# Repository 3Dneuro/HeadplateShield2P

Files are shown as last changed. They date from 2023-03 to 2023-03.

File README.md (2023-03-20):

# Headplate and light-blocking sleeve for 2P imaging
This system was designed to provide simple and reliable light shielding for 2-photon imaging in awake head-fixed mice (running on a 3D-treadmill with visual stimulation in our case). With this in mind, we optimized for the following criteria:

* No hand-made or improvised components that can add variability to the data quality of each experiment – so no putty, wax or tape.
* Simple connection between the animal’s headplate and the light shielding around the microscope lens, to prevent having to work close to the animal’s head, which can stress animals and impact task performance.
* Quick fastening mechanism (< 1 minute). Animals only have a limited time span for motivated, focused performance. We want to lose as little as possible of that time on setting up the imaging. Ideally, the time between putting the animal on the treadmill and beginning the first imaging sequence should be well below 10 minutes.
* Easy to ensure watertight seal with the skull to prevent leakage of fluid during imaging.
* Cheap and easy to replace/tweak if necessary.

We came up with a two-part solution. One is a circular headplate with a ring that rises up conically to fit around the microscope lens while providing a fluid reservoir for imaging with water-immersed objectives. The headplate has two connectors/holders on the side that can be used for stable head fixation (similar concept to Poort et al. 2015 Neuron, Havenith et al. 2019 Scientific Reports). It is easy to implant on the skull, and then remains stable and watertight for months.

The second component is a light-absorbing conical sleeve which was designed to fit with an Olympus 20x objective, and can be lowered below the rim of the implanted headplate once the animal is head-fixed under the microscope. Since the sleeve is designed to fit snugly underneath the rim of the headplate’s cone, it doesn’t require any extra fastening mechanisms apart from lowering it past the headplate’s rim, making it extremely quick and easy to use. In our experience, lowering the sleeve all the way to the base of the headplate eliminates all stray light in recordings.

A first version of this design was published as [10.5281/zenodo.4547658](https://zenodo.org/record/4547658#.ZBLb5XbMKUn). The current version is a parametric re-make of v1 that allows you to change relevant dimensions of the designs and adjust them to your needs (e.g. diameter and height of the sleeve).

# Parameters

> The parametric design was created in Autodesk Fusion 360. To edit the parameters described below, you will need to import the f3d file into Fusion 360. At time of publication, a free Fusion 360 license for academics/educators was available from Autodesk.

The design can be altered to your needs by modifying the parameters controlling the relevant dimensions (see the video below). The table below contains the parameter names, a description of their function and some relevant notes regarding their impact on the design. A graphical representation of the parameters is available in the form of two drawings, one of the [headplate](https://github.com/3Dneuro/HeadplateShield2P/blob/main/design%20files/Headplate%20drawing.pdf) and one of the [sleeve](https://github.com/3Dneuro/HeadplateShield2P/blob/main/design%20files/Sleeve%20drawing.pdf), that can be found in the design files folder (see preview image below). They demonstrate the precise, physical dimensions corresponding to the parameters. These drawings can be used to easily visualize and determine what parameters should be modified for the changes that you wish to make.

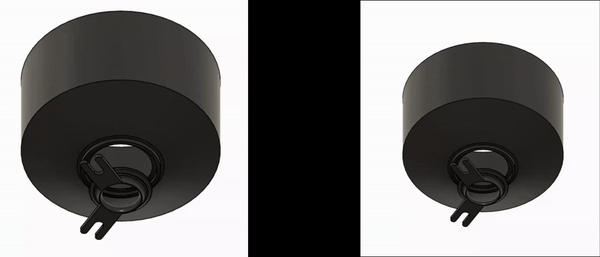
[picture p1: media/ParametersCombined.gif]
Effects of changing parameters #1
 

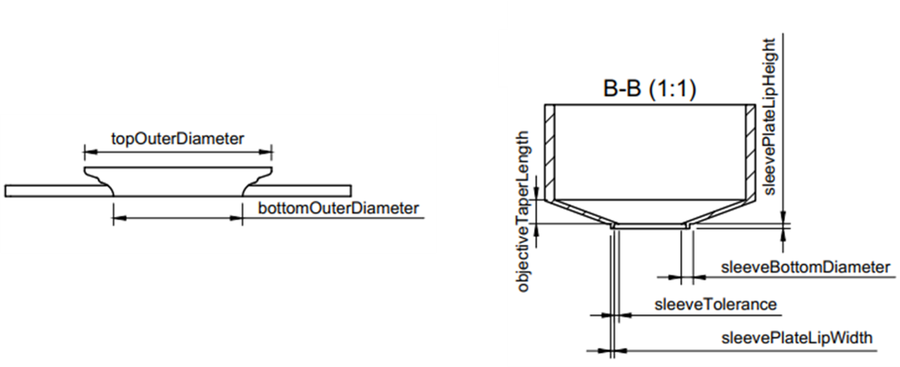
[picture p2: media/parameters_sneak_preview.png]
A selection of editable parameters


## Headplate
| Parameter               | Description                                                                                                       | Notes                                                                                                                                                                                                            |
| ----------------------- | ----------------------------------------------------------------------------------------------------------------- | ---------------------------------------------------------------------------------------------------------------------------------------------------------------------------------------------------------------- |
| bottomInnerDiameter     | The diameter in mm of the opening at the bottom of the headplate                                                  |                                                                                                                                                                                                                  |
| bottomOuterDiameter     | The outer diameter in mm of the bottom of the headplate                                                           |                                                                                                                                                                                                                  |
| topInnerDiameter        | The diameter in mm of the opening at top of the headplate                                                         |                                                                                                                                                                                                                  |
| topOuterDiameter        | The outer diameter in mm of the top of the headplate                                                              | Determines the diameter of the bottom opening in the sleeve as well, ensuring a natural light seal                                                                                                               |
| middleInnerDiameter     | The inner diameter in mm of the hole at the middle of the headplate                                               |                                                                                                                                                                                                                  |
| totalHeight             | The height in mm from the bottom of the headplate to the very top                                                 | Height includes the set height of the lip (topLipHeight)                                                                                                                                                         |
| topLipHeight            | The height in mm of the lip that sits at the top of the headplate                                                 |                                                                                                                                                                                                                  |
| holderLengthFromCenter  | The length in mm of the two holder arms taken with respect to the center of the headplate                         | Solely controls the length of the arms, start of screw openings/slots is not affected                                                                                                                            |
| holderWidth             | The width in mm of the holder arms                                                                                | Does not alter the diameter of the screw openings, can be used to widen or slim the two prongs of each holder                                                                                                    |
| holderOpeninngDiameter  | The diameter in mm of the screw openings in the holder arms                                                       | This determines what size screws should be used to fasten the headplate                                                                                                                                          |
| holderOpeningFromCenter | The distance in mm from the beginning of the screw opening to the center of the headplate                         | Can be used to move the start of the screw openings/slots to or from the center of the headplate                                                                                                                 |
| holderHeight            | The height in mm of the holder arms                                                                               | Height of the holders is limited with respect to the height of the headplate (totalHeight)                                                                                                                       |
| holderAngle             | The angle in degrees of the holder arms with respect to the z midline                                             | Holder configuration can be changed using this parameter. At certain angles, holders can be made to overlap if so desired                                                                                        |

## Sleeve
| Parameter               | Description                                                                                                       | Notes                                                                                                                                                                                                            |
| ----------------------- | ----------------------------------------------------------------------------------------------------------------- | ---------------------------------------------------------------------------------------------------------------------------------------------------------------------------------------------------------------- |
| wallThickness           | The thickness in mm of the walls of the sleeve                                                                    |                                                                                                                                                                                                                  |
| objectiveDiameter       | The inner diameter in mm of the sleeve                                                                            | Using this and objectiveTaperLength, the sleeve can be made to fit specific objectives                                                                                                                           |
| sleeveHeight            | The height in mm of the straight portion of the sleeve (excluding the taper thus)                                 | Can be used to have the sleeve run further up the objective                                                                                                                                                      |
| toleranceSleeve         | The space in mm between the lip on the sleeve and the lip on the headplate                                        | This parameter controls the distance between the sleeve and headplate and thus how well light is sealed out. Less tolerance means less light can reach the opening, however, resutling in less room for movement |
| objectiveTaperLength    | The vertical height in mm of the taper, to be measured from the start of the taper to the bottom of the objective | To ensure a correct fit, measure the distance from the start of the taper on the objective to the bottom as if it were on the midline                                                                            |
| sleeveBottomDiameter    | The outer diameter in mm of the bottom of the sleeve                                                              | Controls the flat area at the bottom of the sleeve, a higher outer diameter increases the surface area upon which the sealing lip is located allowing for more tolerance if needed                               |
| sleevePlateLipWidth     | The width in mm of the sealing lip at the bottom of the sleeve                                                    | The max width dependents on the surface area at the bottom of the sleeve, adjust sleeveBottomDiameter when required to do so                                                                                     |
| sleevePlateLipHeight    | The height in mm of the sealing lip at the bottom of the sleeve                                                   |                                                                                                                                                                                                                  |

# Manufacturing
While the headplate can be produced in a range of materials, we recommend machined aluminum, which is strong enough to ensure stable imaging-compatible head fixation while still being light. For test purposes, printing the headplate in a sturdy plastic can work well.
The sleeve can be made in any opaque plastic, preferably one that is matte/does not reflect stray light, or be machined in aluminum.

# License
> Copyright 3Dneuro 2022.
> This source describes Open Hardware and is licensed under the CERN-OHL-S v2
> You may redistribute and modify this documentation and make products using it under the terms of the CERN-OHL-S v2 (https:/cern.ch/cern-ohl). This documentation is distributed WITHOUT ANY EXPRESS OR IMPLIED WARRANTY, INCLUDING OF MERCHANTABILITY, SATISFACTORY QUALITY AND FITNESS FOR A PARTICULAR PURPOSE. Please see the CERN-OHL-S v2 for applicable conditions.
> Source location: https://www.3dneuro.com/open-hardware/
> https://choosealicense.com/licenses/cern-ohl-s-2.0/

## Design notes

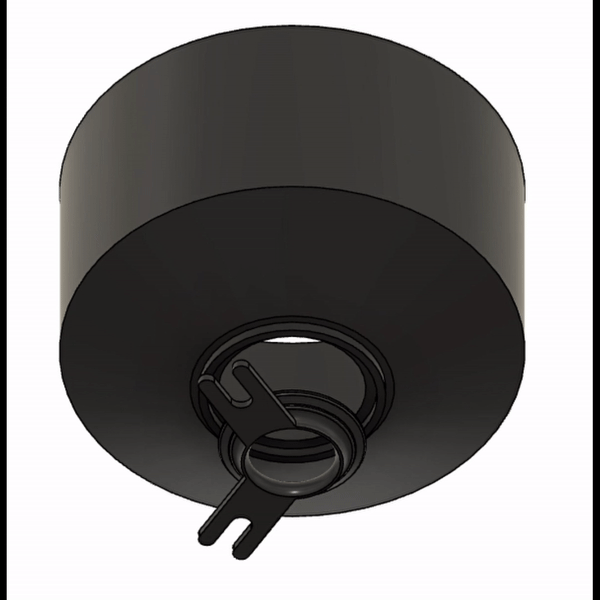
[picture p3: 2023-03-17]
media/Parameters2.gif

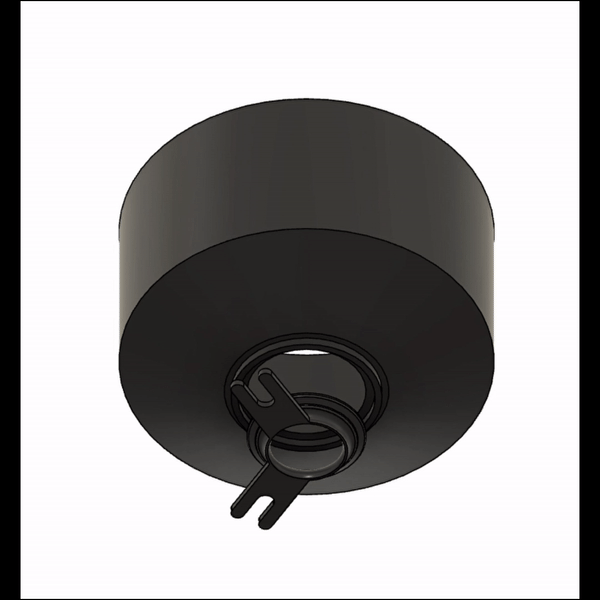
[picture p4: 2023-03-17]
media/Parameters1.gif

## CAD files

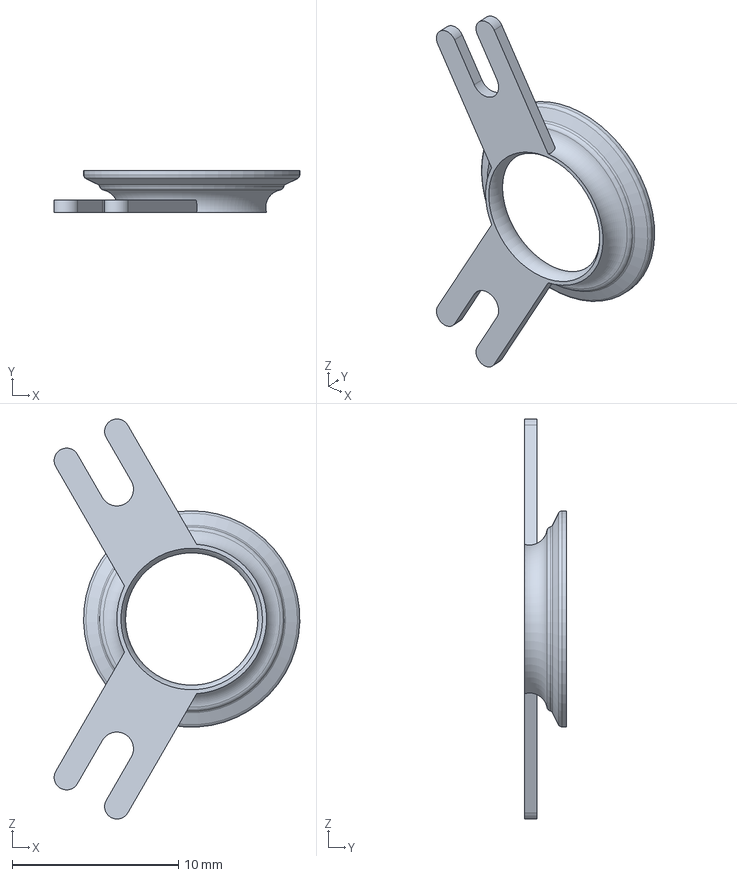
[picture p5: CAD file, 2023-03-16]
design files/Headplate.step
14.8 x 2.50 x 24.0 mm

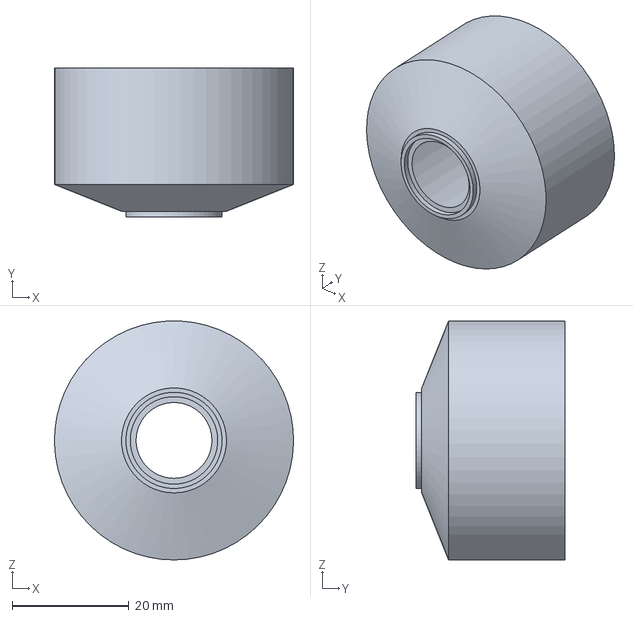
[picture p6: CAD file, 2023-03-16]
design files/2p Sleeve.step
41.0 x 25.6 x 41.0 mm

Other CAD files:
design files/2p Sleeve.stl
design files/HeadplateShield2P v1.f3d

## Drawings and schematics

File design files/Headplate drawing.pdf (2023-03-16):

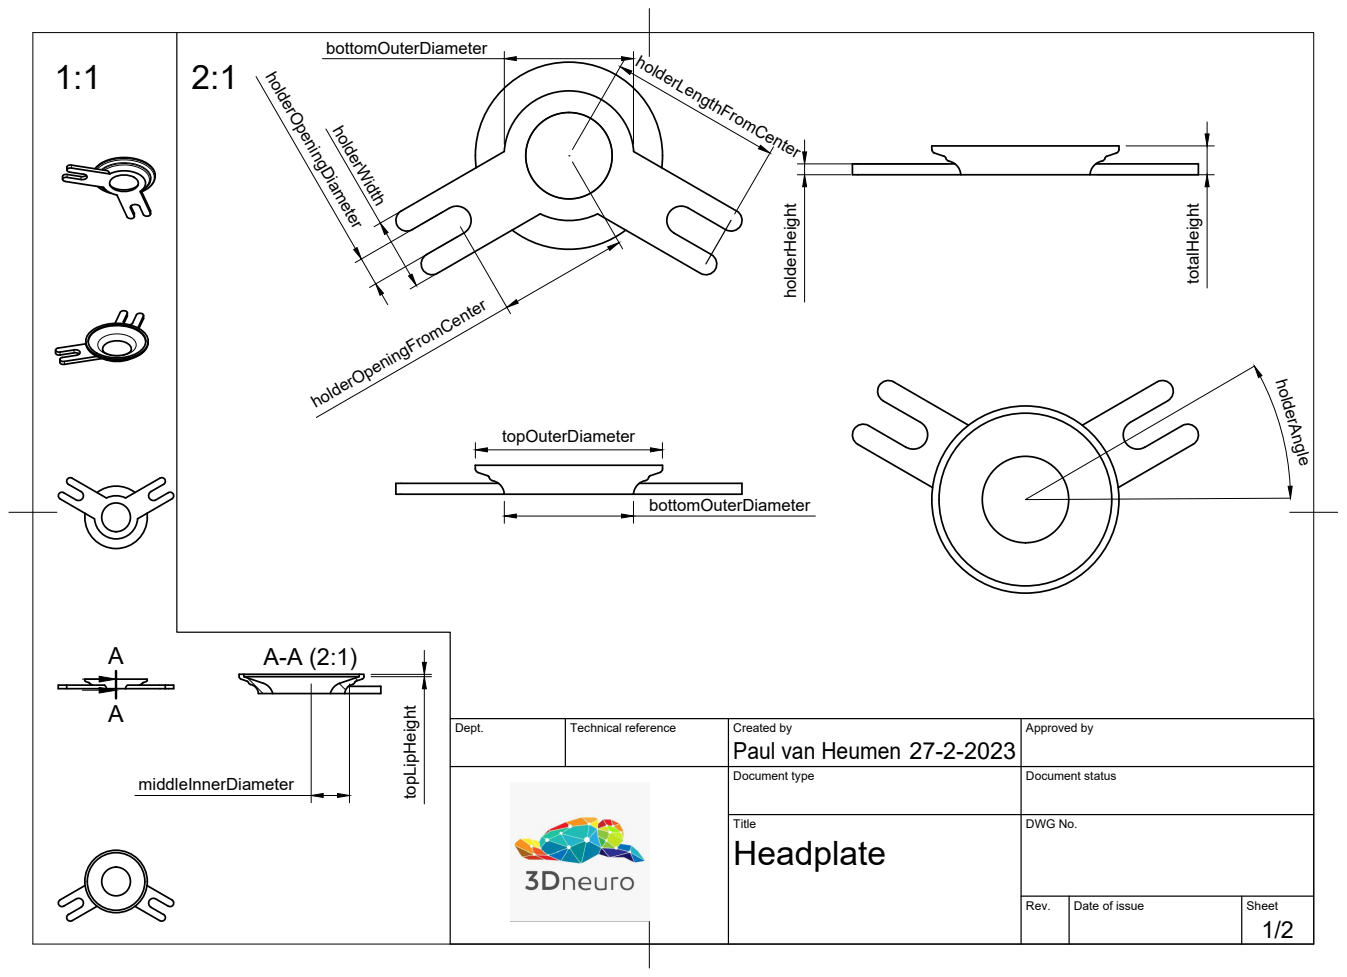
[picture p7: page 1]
middleInnerDiameter; topLipHeight; totalHeight holderHeight; holderWidth holderOpeningDiameter

Dept. | Technical reference | Created by Paul van Heumen 27-2-2023 | Approved by

Document type | Document status

Title Headplate | DWG No.

Rev. | Date of issue | Sheet 1/2

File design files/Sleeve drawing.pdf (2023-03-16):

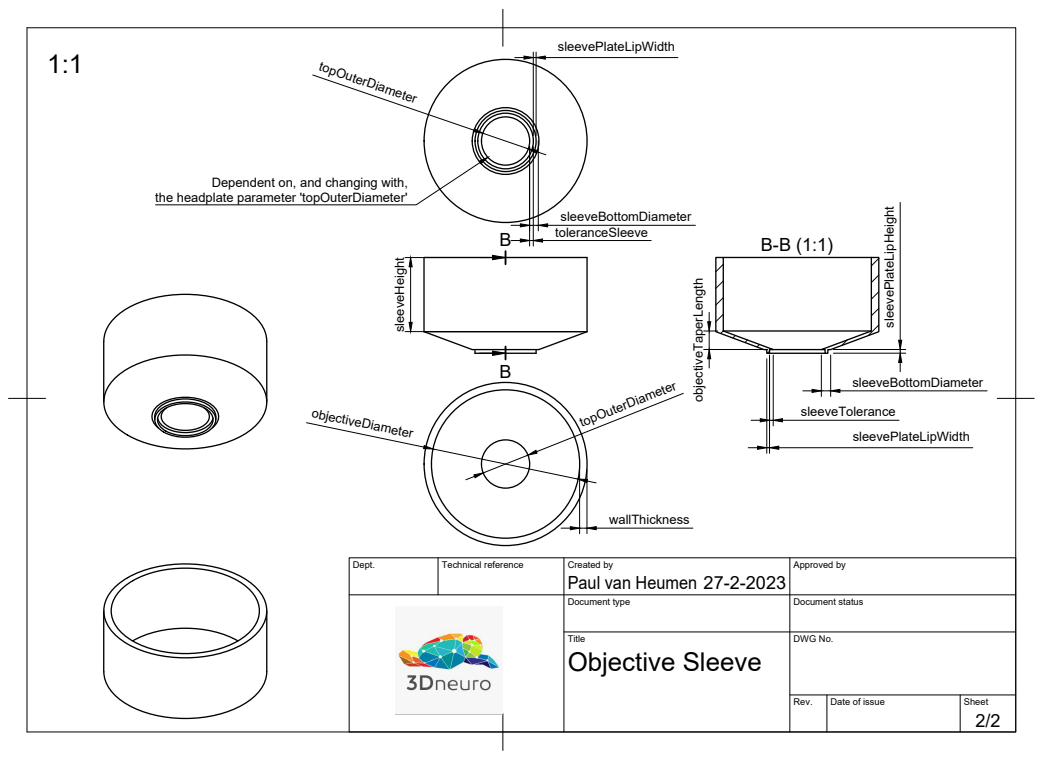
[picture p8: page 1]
sleevePlateLipWidth sleeveHeight; objectiveTaperLength

Dependent on, and changing with,

the headplate parameter 'topOuterDiameter'

topOuterDiameter objectiveDiameter sleevePlateLipHeight

Dept. | Technical reference | Created by Paul van Heumen 27-2-2023 | Approved by

Document type | Document status

Title Objective Sleeve | DWG No.

Rev. | Date of issue | Sheet 2/2
